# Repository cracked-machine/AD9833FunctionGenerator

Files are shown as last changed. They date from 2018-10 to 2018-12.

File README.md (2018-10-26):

# DDS Function Generator
## Specification
- Produces sine, square, triange output
- Output waveform resolution of 0.1 Hz
- Frequency range: 1Hz - 100KHz
- Selectable ranges: 0-1KHz, 0-10KHz, 0-100KHz
- Frequency sweep mode with lower/upper range and speed control.
- Output amplitude up to 10 V peak-to-peak (+20dBv)
- DC offset voltage adjustable between -10V to +10V
- Output impedance of 600 Ω.

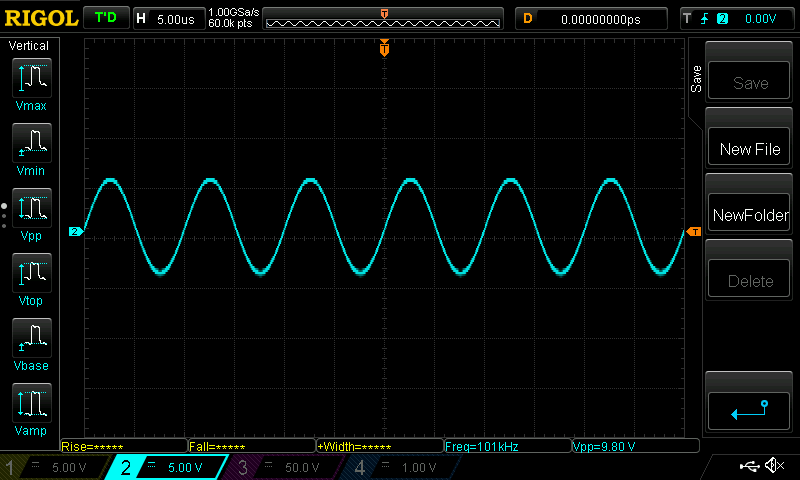
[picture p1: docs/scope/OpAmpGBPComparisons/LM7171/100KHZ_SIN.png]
100KHz Sine Wave @ 10vpp


---

## Improved signal integrity at 100KHz
This is the square wave signal with +20dBv gain @ 10KHz

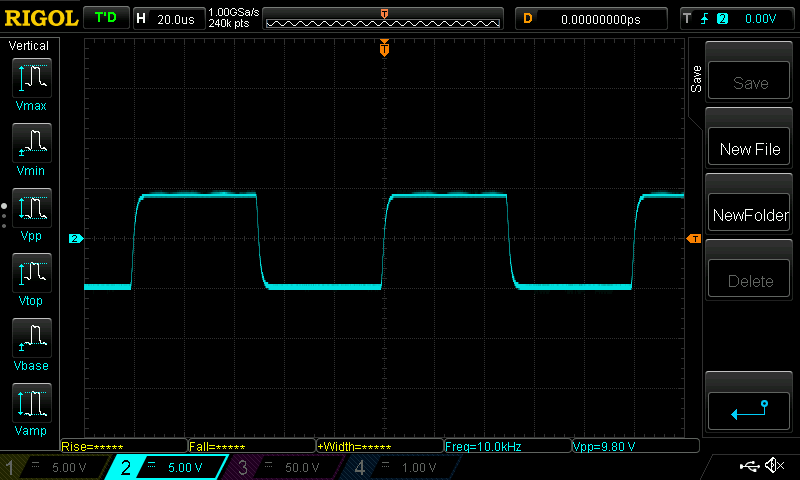
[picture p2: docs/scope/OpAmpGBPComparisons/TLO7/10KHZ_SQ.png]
10KHz Square Wave @ 10vpp using TL071 opamp


This is the same signal @ 100KHz. You can see the TL071 opamp (3MHz Unity GBP) is unable to amplify the huge number of odd-integer harmonics of the waveform. This has an undesirable bandpass filter effect on the signal.

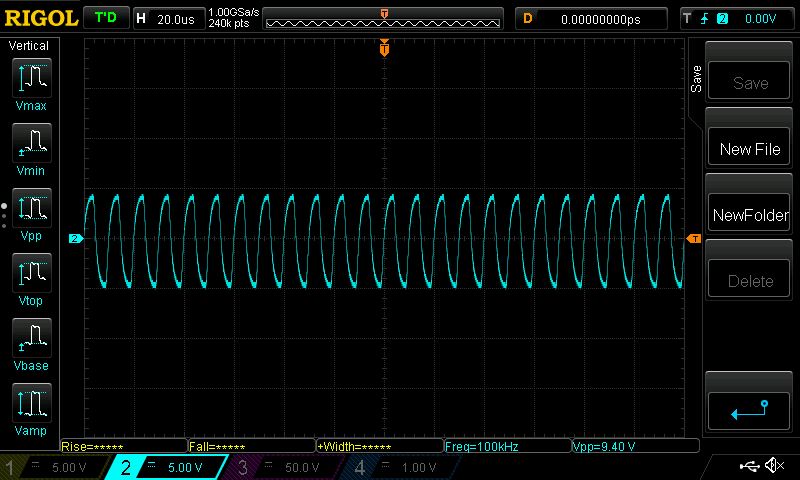
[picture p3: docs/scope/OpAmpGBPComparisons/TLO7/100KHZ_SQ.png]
100KHz Square Wave @ 10vpp using TL071 opamp


The LM7171 opamp (200MHz Unity GBP) is able to maintain the square wave harmonics for +20dBv @ 100KHz.  

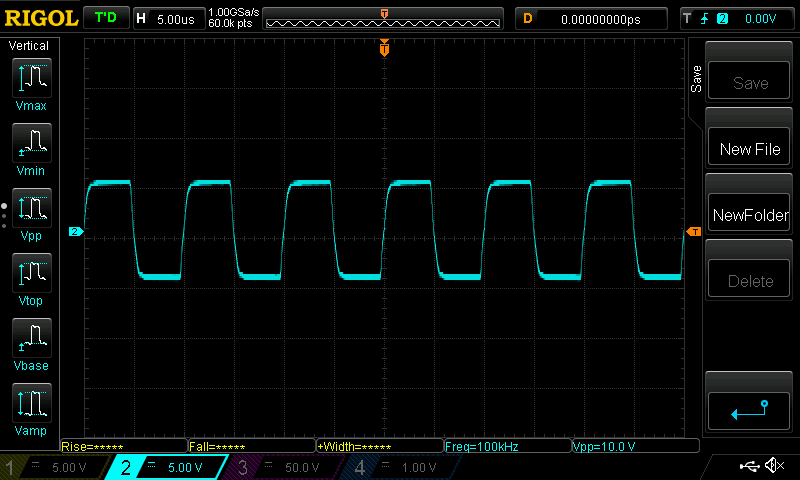
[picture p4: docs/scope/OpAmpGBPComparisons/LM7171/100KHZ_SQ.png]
100KHz Square Wave @ 10vpp using LM7171 opamp


---

## Schematic

[Schematic](https://github.com/cracked-machine/AD9833FunctionGenerator/blob/master/docs/Schematic/AD9833FunctionGenerator.pdf)

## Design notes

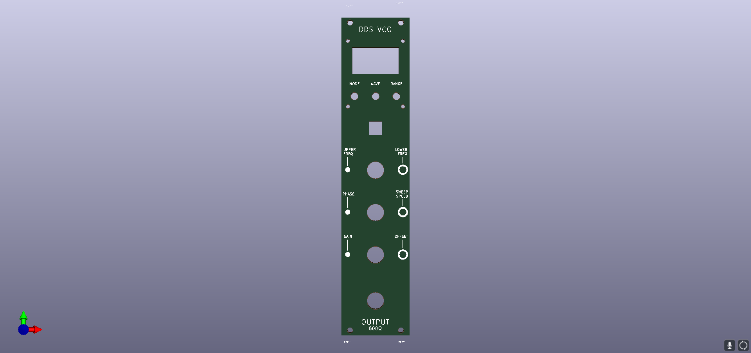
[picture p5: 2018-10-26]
docs/FrontPanel/FrontPanel.png

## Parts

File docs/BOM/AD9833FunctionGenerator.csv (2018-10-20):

Reference | Value | Footprint | Datasheet | MouserPartNo
J_AD9833 | Conn_01x07 | Connector_PinSocket_2.54mm:PinSocket_1x07_P2.54mm_Vertical
C1 | 220nF | Capacitor_SMD:C_0805_2012Metric_Pad1.15x1.40mm_HandSolder
C2 | 100nF | Capacitor_SMD:C_0805_2012Metric_Pad1.15x1.40mm_HandSolder
U1 | LM7805_TO220 | Package_TO_SOT_THT:TO-220-3_Vertical | http://www.fairchildsemi.com/ds/LM/LM7805.pdf | 926-LM7805CT/NOPB
R_VEL1 | 100R | Resistor_SMD:R_0805_2012Metric_Pad1.15x1.40mm_HandSolder | ~
J_OUT1 | Conn_01x02 | Connector_PinSocket_2.54mm:PinSocket_1x02_P2.54mm_Vertical | ~
J_PWR1 | Conn_02x05_Odd_Even | Connector_PinHeader_2.54mm:PinHeader_2x05_P2.54mm_Vertical | ~
U_POT1 | MCP42050 | Package_SO:SOIC-14_3.9x8.7mm_P1.27mm | http://ww1.microchip.com/downloads/en/DeviceDoc/11195c.pdf | 579-MCP42050-I/SL
RV_FREQ1 | B10K | PTH901:PTH901 |  | 652-PTH901-030S-103B
A1 | Arduino_Nano_v3.x | Module:Arduino_Nano | http://www.mouser.com/pdfdocs/Gravitech_Arduino_Nano3_0.pdf
C_POTBP1 | 100nF | Capacitor_SMD:C_0805_2012Metric_Pad1.15x1.40mm_HandSolder | ~
ROFF1 | 1K | Resistor_SMD:R_0805_2012Metric_Pad1.15x1.40mm_HandSolder | ~
ROFF2 | 1K | Resistor_SMD:R_0805_2012Metric_Pad1.15x1.40mm_HandSolder | ~
SW_PWR1 | SW_DPDT_x2 | ALPS_SPUN191600:ALPS_SPUN191600
RV_TIME1 | R_POT_Dual_Separate | PTH901:PTH901
R_PHASE1 | 100R | Resistor_SMD:R_0805_2012Metric_Pad1.15x1.40mm_HandSolder | ~
CPWRBP2 | 100nF | Capacitor_SMD:C_0805_2012Metric_Pad1.15x1.40mm_HandSolder | ~
CPWRBP1 | 100nF | Capacitor_SMD:C_0805_2012Metric_Pad1.15x1.40mm_HandSolder | ~
J_OLEDCONNECTOR1 | Conn_01x04 | Connector_PinSocket_2.54mm:PinSocket_1x04_P2.54mm_Vertical
SW_MODE1 | SW_SPST | Button_Switch_THT:SW_PUSH_6mm |  | 688-SKHHDJA010
SW_FUNC1 | SW_SPST | Button_Switch_THT:SW_PUSH_6mm |  | 688-SKHHDJA010
R_MODE1 | 1K | Resistor_SMD:R_0805_2012Metric_Pad1.15x1.40mm_HandSolder | ~
R_FUNC1 | 1K | Resistor_SMD:R_0805_2012Metric_Pad1.15x1.40mm_HandSolder | ~
SW_RANGE1 | SW_SPST | Button_Switch_THT:SW_PUSH_6mm |  | 688-SKHHDJA010
R_RANGE1 | 1K | Resistor_SMD:R_0805_2012Metric_Pad1.15x1.40mm_HandSolder | ~
J_AUX2MAIN2 | Conn_02x05_Odd_Even | Connector_PinHeader_2.54mm:PinHeader_2x05_P2.54mm_Vertical | ~
J_MAIN2AUX1 | Conn_02x05_Odd_Even | Connector_PinHeader_2.54mm:PinHeader_2x05_P2.54mm_Vertical | ~
R_MIX2 | 1K | Resistor_SMD:R_0805_2012Metric_Pad1.15x1.40mm_HandSolder | ~
R_MIX1 | 1K | Resistor_SMD:R_0805_2012Metric_Pad1.15x1.40mm_HandSolder | ~
R_ISO1 | 600R 1% | Resistor_SMD:R_0805_2012Metric_Pad1.15x1.40mm_HandSolder | ~
RV_UPOFF1 | 100K | Potentiometer_THT:Potentiometer_Piher_PT-6-V_Vertical | ~ | 652-3296Y-1-104LF
C_GAIN1 | 470pF | Capacitor_SMD:C_0805_2012Metric_Pad1.15x1.40mm_HandSolder | ~
RV_AMP1 | B10K | PTH901:PTH901 |  | 652-PTH901-030S-103B
C_MIXBP2 | 100nF | Capacitor_SMD:C_0805_2012Metric_Pad1.15x1.40mm_HandSolder | ~
C_MIXBP3 | 100nF | Capacitor_SMD:C_0805_2012Metric_Pad1.15x1.40mm_HandSolder | ~
RV_LOWOFF1 | 100K | Potentiometer_THT:Potentiometer_Piher_PT-6-V_Vertical | ~ | 652-3296Y-1-104LF
TP_OFF1 | TestPoint | TestPoint:TestPoint_Pad_D2.0mm | ~
R_LOFF1 | 1K | Resistor_SMD:R_0805_2012Metric_Pad1.15x1.40mm_HandSolder | ~
R_HIOFF1 | 1K | Resistor_SMD:R_0805_2012Metric_Pad1.15x1.40mm_HandSolder | ~
RF1 | 1k | Resistor_SMD:R_0805_2012Metric_Pad1.15x1.40mm_HandSolder | ~
RG1 | 1k | Resistor_SMD:R_0805_2012Metric_Pad1.15x1.40mm_HandSolder | ~
RF2 | 8K2 | Resistor_SMD:R_0805_2012Metric_Pad1.15x1.40mm_HandSolder | ~
R_MIX3 | 1K | Resistor_SMD:R_0805_2012Metric_Pad1.15x1.40mm_HandSolder | ~
U_BUFF1 | LM7171 | Package_SO:SOIC-8_3.9x4.9mm_P1.27mm
U_MIX1 | LM7171 | Package_SO:SOIC-8_3.9x4.9mm_P1.27mm
C_MIXBP1 | 2.2uF | Capacitor_SMD:C_0805_2012Metric_Pad1.15x1.40mm_HandSolder | ~
C_MIXBP4 | 2.2uF | Capacitor_SMD:C_0805_2012Metric_Pad1.15x1.40mm_HandSolder | ~
C_BUFFBP2 | 100nF | Capacitor_SMD:C_0805_2012Metric_Pad1.15x1.40mm_HandSolder | ~
C_BUFFBP3 | 100nF | Capacitor_SMD:C_0805_2012Metric_Pad1.15x1.40mm_HandSolder | ~
C_BUFFBP1 | 2.2uF | Capacitor_SMD:C_0805_2012Metric_Pad1.15x1.40mm_HandSolder | ~
C_BUFFBP4 | 2.2uF | Capacitor_SMD:C_0805_2012Metric_Pad1.15x1.40mm_HandSolder | ~
CF2 | 2pF | Capacitor_SMD:C_0805_2012Metric_Pad1.15x1.40mm_HandSolder | ~
CF1 | 2pF | Capacitor_SMD:C_0805_2012Metric_Pad1.15x1.40mm_HandSolder | ~

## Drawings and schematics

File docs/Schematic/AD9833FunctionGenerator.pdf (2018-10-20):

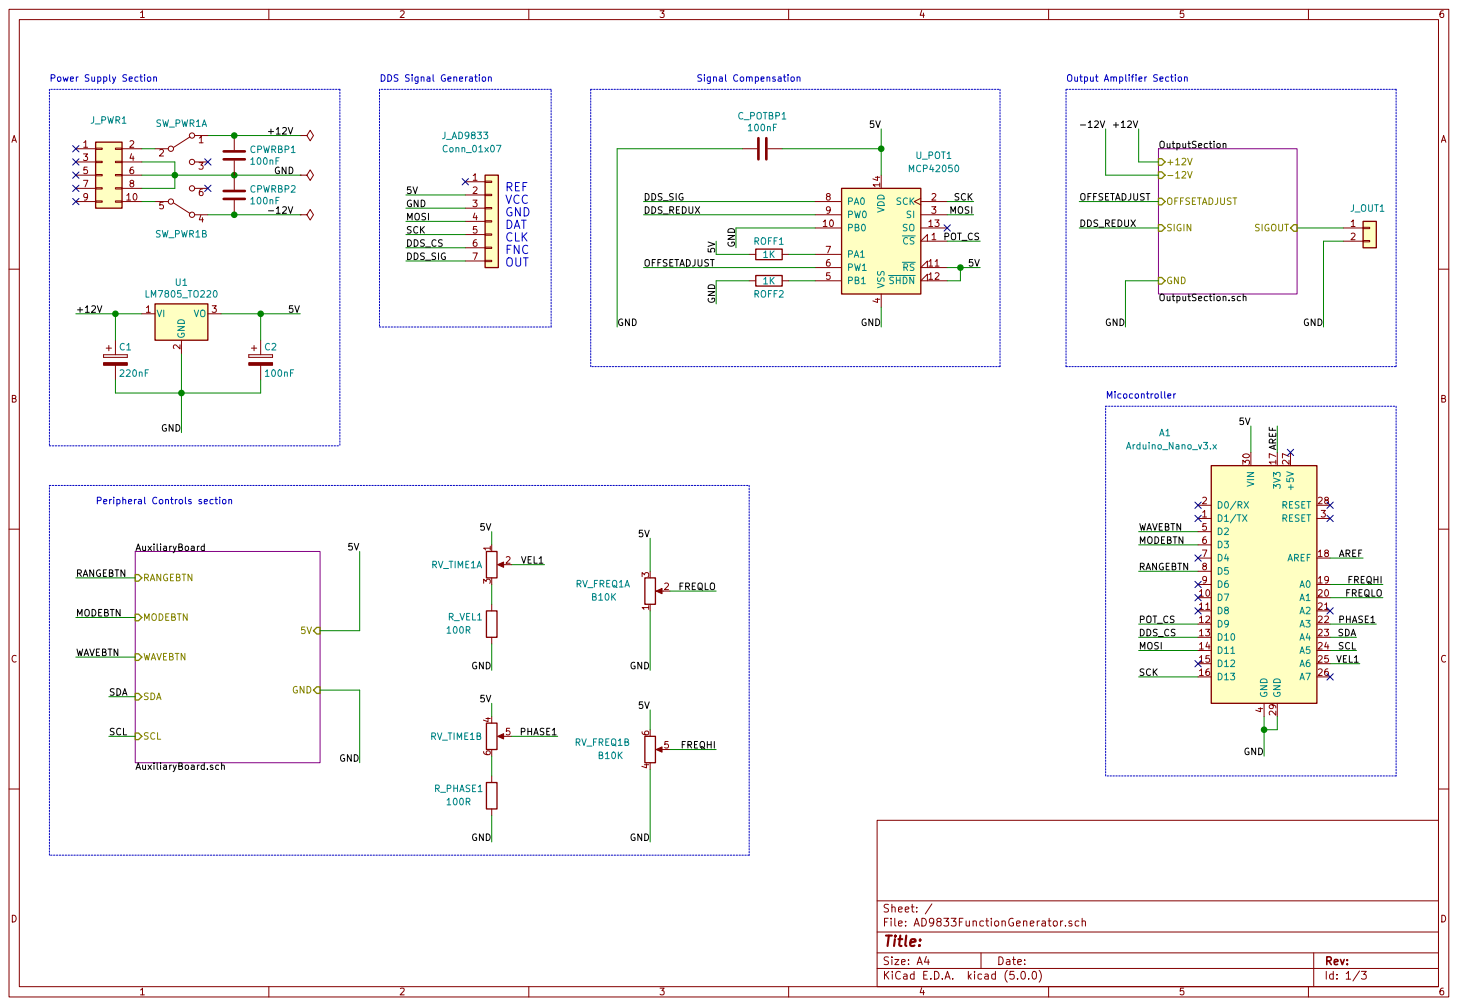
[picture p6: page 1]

Peripheral Controls section WAVEBTN MODEBTN

Id: 1/3 Title: File: AD9833FunctionGenerator.sch Sheet: /

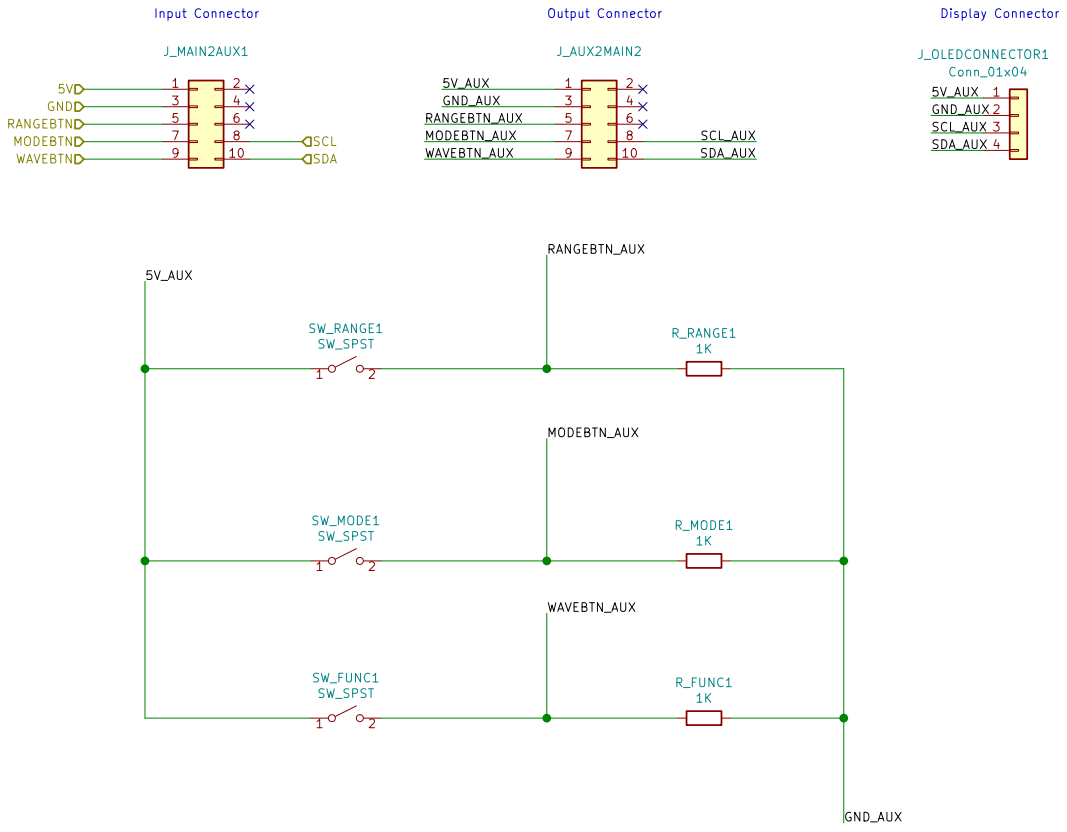
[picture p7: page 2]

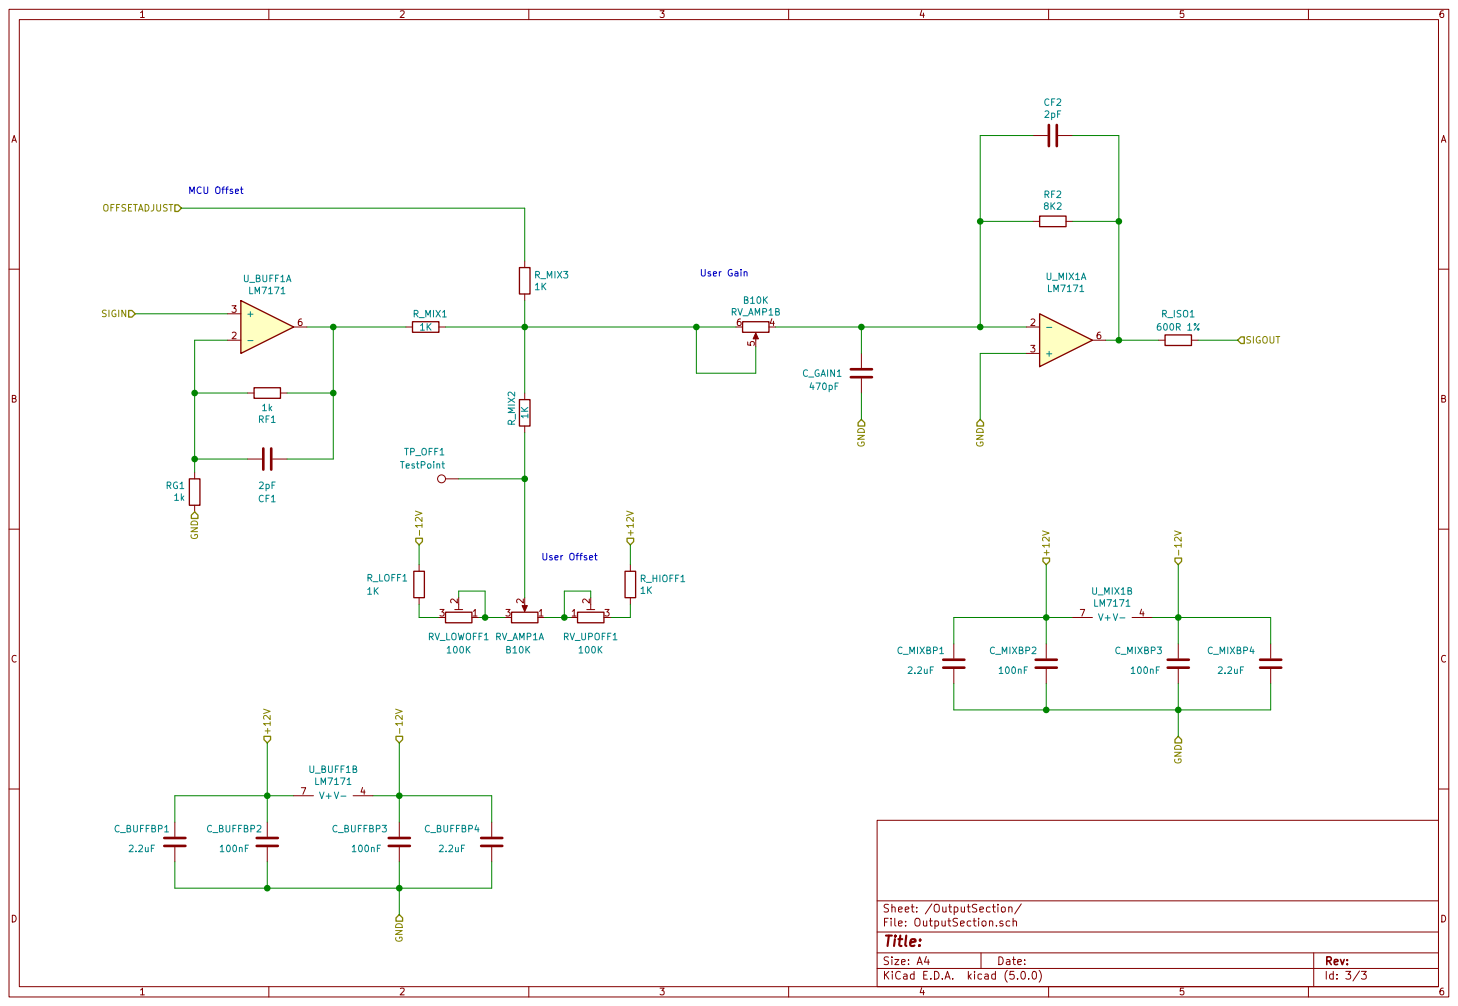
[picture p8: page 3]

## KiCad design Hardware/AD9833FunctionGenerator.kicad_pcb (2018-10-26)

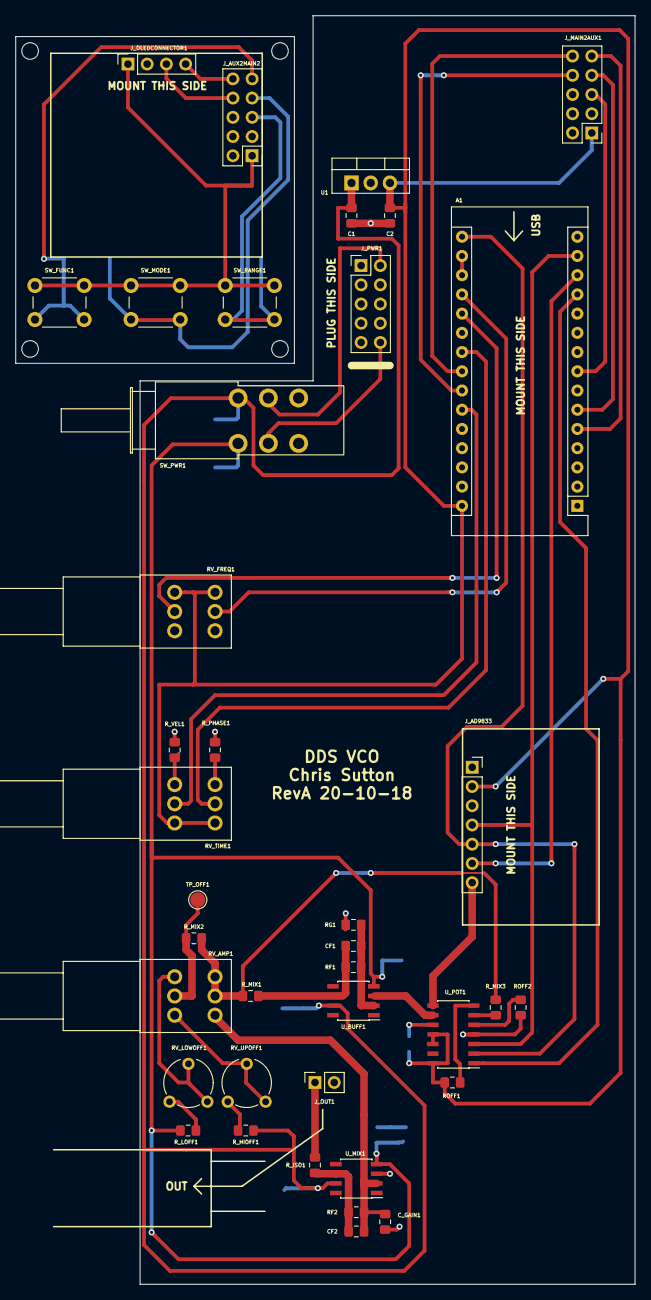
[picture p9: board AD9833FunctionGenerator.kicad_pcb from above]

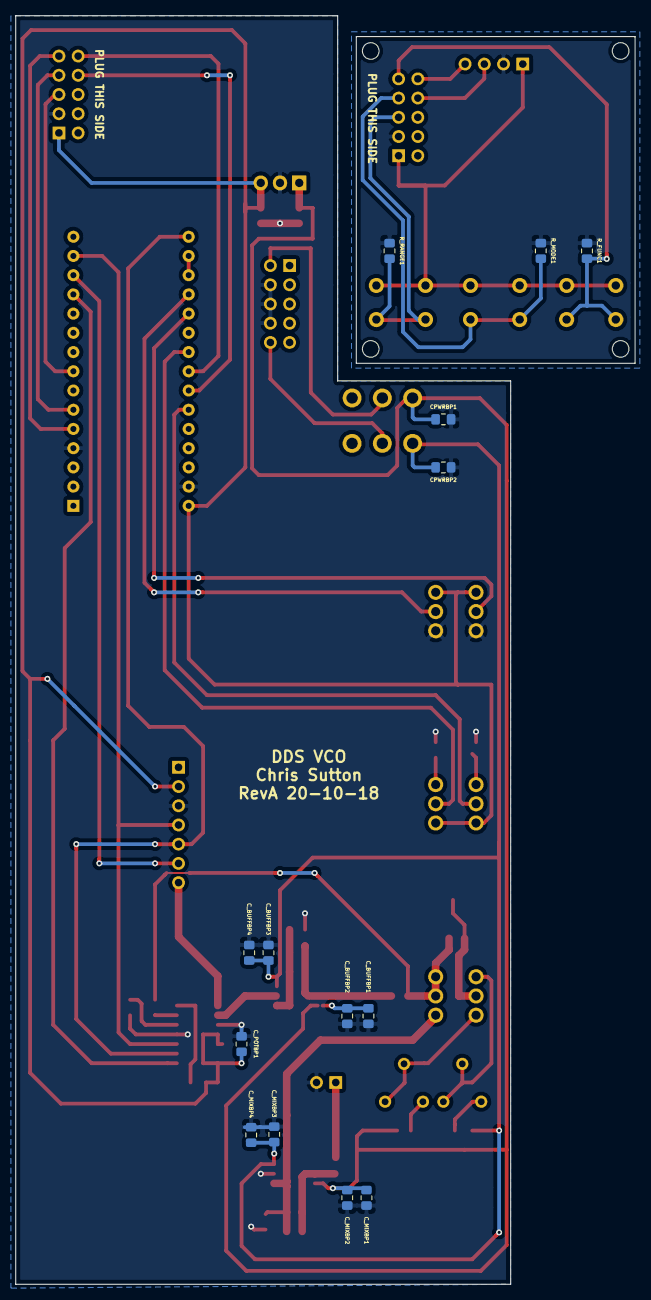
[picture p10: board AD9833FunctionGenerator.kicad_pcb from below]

Board: 2 copper layers, 81.8 x 167.6 mm, 53 parts (14 on the bottom side), 45 nets.

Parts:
A1: Arduino_Nano_v3.x; Arduino_Nano
C1: 220nF; C_0805_2012Metric_Pad1.15x1.40mm_HandSolder
C2: 100nF; C_0805_2012Metric_Pad1.15x1.40mm_HandSolder
CF1, CF2: 2pF; C_0805_2012Metric_Pad1.15x1.40mm_HandSolder
CPWRBP1, CPWRBP2: 100nF; C_0805_2012Metric_Pad1.15x1.40mm_HandSolder
C_BUFFBP1, C_BUFFBP4: 2.2uF; C_0805_2012Metric_Pad1.15x1.40mm_HandSolder
C_BUFFBP2, C_BUFFBP3: 100nF; C_0805_2012Metric_Pad1.15x1.40mm_HandSolder
C_GAIN1: 470pF; C_0805_2012Metric_Pad1.15x1.40mm_HandSolder
C_MIXBP1, C_MIXBP4: 2.2uF; C_0805_2012Metric_Pad1.15x1.40mm_HandSolder
C_MIXBP2, C_MIXBP3: 100nF; C_0805_2012Metric_Pad1.15x1.40mm_HandSolder
C_POTBP1: 100nF; C_0805_2012Metric_Pad1.15x1.40mm_HandSolder
J_AD9833: Conn_01x07; PinSocket_1x07_P2.54mm_Vertical
J_AUX2MAIN2: Conn_02x05_Odd_Even; PinHeader_2x05_P2.54mm_Vertical
J_MAIN2AUX1: Conn_02x05_Odd_Even; PinHeader_2x05_P2.54mm_Vertical
J_OLEDCONNECTOR1: Conn_01x04; PinSocket_1x04_P2.54mm_Vertical
J_OUT1: Conn_01x02; PinSocket_1x02_P2.54mm_Vertical
J_PWR1: Conn_02x05_Odd_Even; PinHeader_2x05_P2.54mm_Vertical
RF1: 1k; R_0805_2012Metric_Pad1.15x1.40mm_HandSolder
RF2: 8K2; R_0805_2012Metric_Pad1.15x1.40mm_HandSolder
RG1: 1k; R_0805_2012Metric_Pad1.15x1.40mm_HandSolder
ROFF1, ROFF2: 1K; R_0805_2012Metric_Pad1.15x1.40mm_HandSolder
RV_AMP1: B10K; PTH901
RV_FREQ1: B10K; PTH901
RV_LOWOFF1: 100K; Potentiometer_Piher_PT-6-V_Vertical
RV_TIME1: R_POT_Dual_Separate; PTH901
RV_UPOFF1: 100K; Potentiometer_Piher_PT-6-V_Vertical
R_FUNC1: 1K; R_0805_2012Metric_Pad1.15x1.40mm_HandSolder
R_HIOFF1: 1K; R_0805_2012Metric_Pad1.15x1.40mm_HandSolder
R_ISO1: 600R 1%; R_0805_2012Metric_Pad1.15x1.40mm_HandSolder
R_LOFF1: 1K; R_0805_2012Metric_Pad1.15x1.40mm_HandSolder
R_MIX1, R_MIX2, R_MIX3: 1K; R_0805_2012Metric_Pad1.15x1.40mm_HandSolder
R_MODE1: 1K; R_0805_2012Metric_Pad1.15x1.40mm_HandSolder
R_PHASE1: 100R; R_0805_2012Metric_Pad1.15x1.40mm_HandSolder
R_RANGE1: 1K; R_0805_2012Metric_Pad1.15x1.40mm_HandSolder
R_VEL1: 100R; R_0805_2012Metric_Pad1.15x1.40mm_HandSolder
SW_FUNC1: SW_SPST; SW_PUSH_6mm
SW_MODE1: SW_SPST; SW_PUSH_6mm
SW_PWR1: SW_DPDT_x2; ALPS_SPUN191600
SW_RANGE1: SW_SPST; SW_PUSH_6mm
TP_OFF1: TestPoint; TestPoint_Pad_D2.0mm
U1: LM7805_TO220; TO-220-3_Vertical
U_BUFF1: LM7171; SOIC-8_3.9x4.9mm_P1.27mm
U_MIX1: LM7171; SOIC-8_3.9x4.9mm_P1.27mm
U_POT1: MCP42050; SOIC-14_3.9x8.7mm_P1.27mm

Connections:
/5V: A1.30, C2.1, C_POTBP1.1, J_AD9833.2, J_MAIN2AUX1.1, ROFF1.2, RV_FREQ1.3, RV_FREQ1.6, RV_TIME1.1, RV_TIME1.4, U1.3, U_POT1.11, U_POT1.12, U_POT1.14
/+12V: C1.1, CPWRBP1.1, C_BUFFBP1.1, C_BUFFBP2.1, C_MIXBP1.1, C_MIXBP2.1, R_HIOFF1.1, SW_PWR1.1, U1.1, U_BUFF1.7, U_MIX1.7
/-12V: CPWRBP2.2, C_BUFFBP3.1, C_BUFFBP4.1, C_MIXBP3.1, C_MIXBP4.1, R_LOFF1.1, SW_PWR1.4, U_BUFF1.4, U_MIX1.4
/AREF: A1.17, A1.18
/AuxiliaryBoard/5V_AUX: J_AUX2MAIN2.1, J_OLEDCONNECTOR1.1, SW_FUNC1.1, SW_MODE1.1, SW_RANGE1.1
/AuxiliaryBoard/GND_AUX: J_AUX2MAIN2.3, J_OLEDCONNECTOR1.2, R_FUNC1.1, R_MODE1.1, R_RANGE1.1
/AuxiliaryBoard/MODEBTN_AUX: J_AUX2MAIN2.7, R_MODE1.2, SW_MODE1.2
/AuxiliaryBoard/RANGEBTN_AUX: J_AUX2MAIN2.5, R_RANGE1.2, SW_RANGE1.2
/AuxiliaryBoard/SCL_AUX: J_AUX2MAIN2.8, J_OLEDCONNECTOR1.3
/AuxiliaryBoard/SDA_AUX: J_AUX2MAIN2.10, J_OLEDCONNECTOR1.4
/AuxiliaryBoard/WAVEBTN_AUX: J_AUX2MAIN2.9, R_FUNC1.2, SW_FUNC1.2
/DDS_CS: A1.13, J_AD9833.6
/DDS_REDUX: U_BUFF1.3, U_POT1.9
/DDS_SIG: J_AD9833.7, U_POT1.8
/FREQHI: A1.19, RV_FREQ1.5
/FREQLO: A1.20, RV_FREQ1.2
/GND: A1.4, A1.29, C1.2, C2.2, CPWRBP1.2, CPWRBP2.1, C_BUFFBP1.2, C_BUFFBP2.2, C_BUFFBP3.2, C_BUFFBP4.2, C_GAIN1.2, C_MIXBP1.2, C_MIXBP2.2, C_MIXBP3.2, C_MIXBP4.2, C_POTBP1.2, J_AD9833.3, J_MAIN2AUX1.3, J_OUT1.2, J_PWR1.4, J_PWR1.6, J_PWR1.8, RG1.1, ROFF2.2, RV_FREQ1.1, RV_FREQ1.4, R_PHASE1.1, R_VEL1.1, U1.2, U_MIX1.3, U_POT1.4, U_POT1.10
/MODEBTN: A1.6, J_MAIN2AUX1.7
/MOSI: A1.14, J_AD9833.4, U_POT1.3
/OFFSETADJUST: R_MIX3.1, U_POT1.6
/OutputSection/SIGOUT: J_OUT1.1, R_ISO1.1
/PHASE1: A1.22, RV_TIME1.5
/POT_CS: A1.12, U_POT1.1
/RANGEBTN: A1.8, J_MAIN2AUX1.5
/SCK: A1.16, J_AD9833.5, U_POT1.2
/SCL: A1.24, J_MAIN2AUX1.8
/SDA: A1.23, J_MAIN2AUX1.10
/VEL1: A1.25, RV_TIME1.2
/WAVEBTN: A1.5, J_MAIN2AUX1.9
unnamed: CF1.1, RF1.1, R_MIX1.1, U_BUFF1.6
unnamed: CF1.2, RF1.2, RG1.2, U_BUFF1.2
unnamed: CF2.1, RF2.1, R_ISO1.2, U_MIX1.6
unnamed: CF2.2, C_GAIN1.1, RF2.2, RV_AMP1.4, U_MIX1.2
unnamed: J_PWR1.2, SW_PWR1.2
unnamed: J_PWR1.10, SW_PWR1.5
unnamed: ROFF1.1, U_POT1.7
unnamed: ROFF2.1, U_POT1.5
unnamed: RV_AMP1.1, RV_UPOFF1.1, RV_UPOFF1.2
unnamed: RV_AMP1.2, R_MIX2.1, TP_OFF1.1
unnamed: RV_AMP1.3, RV_LOWOFF1.1, RV_LOWOFF1.2
unnamed: RV_AMP1.5, RV_AMP1.6, R_MIX1.2, R_MIX2.2, R_MIX3.2
unnamed: RV_LOWOFF1.3, R_LOFF1.2
unnamed: RV_TIME1.3, R_VEL1.2
unnamed: RV_TIME1.6, R_PHASE1.2
unnamed: RV_UPOFF1.3, R_HIOFF1.2

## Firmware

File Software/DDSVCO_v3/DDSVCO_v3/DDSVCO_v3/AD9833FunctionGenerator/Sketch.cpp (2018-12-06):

/*Begining of Auto generated code by Atmel studio */
#include <Arduino.h>

/*End of auto generated code by Atmel studio */

#include <TimerOne.h>

#include "BinaryUtils.h"
#include "dds.h"
#include "adc.h"
#include "oled.h"
#include "pcint.h"
//#include "spi_utils.h"
//Beginning of Auto generated function prototypes by Atmel Studio
void doTimer1Int();
//End of Auto generated function prototypes by Atmel Studio




volatile const uint8_t adc0 = (1<<ADLAR) | 0;
volatile const uint8_t adc1 = (1<<ADLAR) | 1;
int gain, offset;
int tmp = 0;

volatile int ohms = 0;


// controls the mode behavior (sweep/normal)
void doTimer1Int()
{ 
  
  dds_callback_func();

}

void setup() 
{
  Serial.begin(9600);
  
  Timer1.initialize(clkspeed);
  Timer1.attachInterrupt(doTimer1Int);
  
  setup_pcint();

  adc_setup();
  oled_setup();
  
  
  
  pinMode (digipot_ss_pin, OUTPUT);
  digitalWrite(digipot_ss_pin, HIGH);
  pinMode (dds_ss_pin, OUTPUT);
  digitalWrite(dds_ss_pin, HIGH);
  SPI.begin();
  
  digipot_write_spi(MCP_WRITEPB0, TriUnityLvl, digipot_ss_pin);
  digipot_write_spi(MCP_WRITEPB0, SquareUnityLvl, digipot_ss_pin);
  digipot_write_spi(MCP_WRITEPB0, SineUnityLvl, digipot_ss_pin);

  digipot_write_spi(MCP_WRITEPB1, TriOffsetLvl, digipot_ss_pin);
  digipot_write_spi(MCP_WRITEPB1, SquareOffsetLvl, digipot_ss_pin);
  digipot_write_spi(MCP_WRITEPB1, SineOffsetLvl, digipot_ss_pin);
}

void loop() 
{
  oled_draw();
}

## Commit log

2018-09-24 updated sw
    - added five simultaneous ADC interrupts
    - added mode, freq and sweep info to display
    - added 7805 regulator for +/-12V and +5V rails.
    [AD9833FunctionGenerator-2018-09-23-23-28-16.sch, AD9833FunctionGenerator.sch]
2018-09-27 fixed digpot/dds sidebyside spi config
    [AD9833FunctionGenerator.sch]
2018-09-28 added attenuation and amplitude opamp circuit
    [AD9833FunctionGenerator.sch]
2018-09-28 added analog output section for fixed gain compensation, variable offset and variable adjustments
    [AD9833FunctionGenerator.sch]
2018-09-28 Board Layout completed
    [AD9833FunctionGenerator-2018-09-10-23-01-08.sch, AD9833FunctionGenerator.sch]
2018-09-29 Board Layout updated for potentiometer daughter boards
    [AD9833FunctionGenerator.kicad_pcb]
2018-09-29 changed to SMT. Added proper spaces for pots
    [AD9833FunctionGenerator.kicad_pcb, AD9833FunctionGenerator.sch]
2018-09-30 Changed to 4 layer board. Middle layers for 5V and GND. Signal traces on top layer, +/-12V and HF digital signals on bottom layer
    [AD9833FunctionGenerator.kicad_pcb, AD9833FunctionGenerator.sch]
2018-10-01 updated hardware
    - changed output opamp to inverting to allow 0V-20Vpp output
    [AD9833FunctionGenerator.kicad_pcb, AD9833FunctionGenerator.sch]
2018-10-01 save update
    [AD9833FunctionGenerator.kicad_pcb]
2018-10-02 Changed J_PWR1 from 01x03 to 02x05
    [AD9833FunctionGenerator.kicad_pcb, AD9833FunctionGenerator.sch]
2018-10-03 added MCP42050
    [AD9833FunctionGenerator.sch]
2018-10-05 updated SW and HW
    - Added LM7171 output sectionz. 20Vp-p output, +26db gain, no cutoff up to 100KHz.
    - Corrected output section offset controls
    - Added phase control code (not working)
    [AD9833FunctionGenerator.sch]
2018-10-06 updated HW
    - Changed Offset and Amp pots from 50K to 10: (better part availability)
    - Adjusted opamp gain resistors ratio
    - Added 100K trim pots for eaiser offset center adjustment
    [AD9833FunctionGenerator.sch]
2018-10-07 Added custom opamp symbols
    [AD9833FunctionGenerator.sch]
2018-10-07 updated hardware
    [AD9833FunctionGenerator.sch]
2018-10-09 Created board layout RevB. Right-angled to front panel, with front facing aux board(OLED/Buttons)
    [AD9833FunctionGenerator.csv, AD9833FunctionGenerator.kicad_pcb, AD9833FunctionGenerator.sch, AuxiliaryBoard.sch]
2018-10-09 Tidied up schematic. Added sub-sheets
    [AD9833FunctionGenerator.kicad_pcb, AD9833FunctionGenerator.sch, AuxiliaryBoard.sch, OutputSection.sch]
2018-10-10 updated HW
    - Added separate analog and digital ground to prevent output signal ripple/jitter
    [AD9833FunctionGenerator.kicad_pcb, AD9833FunctionGenerator.sch, OutputSection.sch]
2018-10-11 updated HW (output section)
    - Switched VFA LM7171 for CFA LT1227 (improved frequency response)
    - Removed TL071 from output section
    [OutputSection.sch]
2018-10-13 board rev b
    [AD9833FunctionGenerator.kicad_pcb, AD9833FunctionGenerator.sch, OutputSection.sch]
2018-10-14 updated board layout
    [AD9833FunctionGenerator.kicad_pcb, AD9833FunctionGenerator.sch, OutputSection.sch]
2018-10-14 updated hardware
    - resized.relocated drill holes on aux board
    - removed keep out areas for SPI/I2C clock signals
    - Improved GND plane access for return signals
    - rmoved traces from underneath MCP42050
    [AD9833FunctionGenerator.kicad_pcb]
2018-10-15 Removed power traces from ground plane. improved horizontal component distribution. added right-angle PCB mount DPDT power switch.
    [AD9833FunctionGenerator.kicad_pcb, AD9833FunctionGenerator.sch]
2018-10-15 Updated potentimeter footprints
    [AD9833FunctionGenerator.kicad_pcb]
2018-10-16 Added third concentric dual pot for phase feature
    [AD9833FunctionGenerator.kicad_pcb, AD9833FunctionGenerator.sch]
2018-10-16 Updated footprints
    [AD9833FunctionGenerator.kicad_pcb, OutputSection.sch]
2018-10-17 increased size of board layout to accomodate pot clearance.
    [AD9833FunctionGenerator.kicad_pcb, AD9833FunctionGenerator.sch, OutputSection.sch]
2018-10-17 Repositioned Nano module so that USB socket faces upwards
    [AD9833FunctionGenerator.kicad_pcb]
2018-10-18 Reduced size of board width to 90mm
    [AD9833FunctionGenerator.kicad_pcb, AD9833FunctionGenerator.sch, OutputSection.sch]
2018-10-19 Refined board layout
    [AD9833FunctionGenerator.kicad_pcb]
2018-10-19 Draft RevA Board
    [AD9833FunctionGenerator.kicad_pcb, AD9833FunctionGenerator.sch, OutputSection.sch]
2018-10-20 Final REVA
    [AD9833FunctionGenerator-B.Cu.gbr, AD9833FunctionGenerator-B.Mask.gbr, AD9833FunctionGenerator-B.Paste.gbr, AD9833FunctionGenerator-B.SilkS.gbr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]
2018-10-26 created front panel
    [AD9833FunctionGenerator-2018-09-23-23-28-16.sch, AD9833FunctionGenerator.kicad_pcb, AuxiliaryBoard.sch, FrontPanel_AD9833FunctionGenerator-Edge.Cuts.gbr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]
2018-12-05 Imported Arduino sketch to AS7
